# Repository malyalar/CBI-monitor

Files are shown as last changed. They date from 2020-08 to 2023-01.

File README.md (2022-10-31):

# Hematuria monitor

## An open source solution for management and automation of continuous bladder irrigation using off-the-shelf consumer electronics.
Continuous bladder irrigation (CBI), or bladder washout, is a procedure to prevent blood clot formation after urological procedures (prostatic resection, kidney stone removal, et cetera). We believe the process can be augmented through digitized color recognition and wireless updates to the CBI-supervising provider.

## Description
This hematuria monitor ("HM") is an Arduino-controlled device that measures saline flow from the Foley catheter input, through the bladder, and to the outflow collection bag with a load sensor (HX711), and analyzes the absorptivity of outflow irrigate at multiple wavelengths with a visible-light spectrophotometer (AS7262) to non-invasively detect hematuria in the irrigate. It integrates these two datasets to estimate a variety of statistics about the CBI process. In it's current implementation, it can send updates to a custom-built local radio pager (enclosure CAD available, but schematics pending) using a 315mHz transmitter/receiver combo. 

<p float="left">
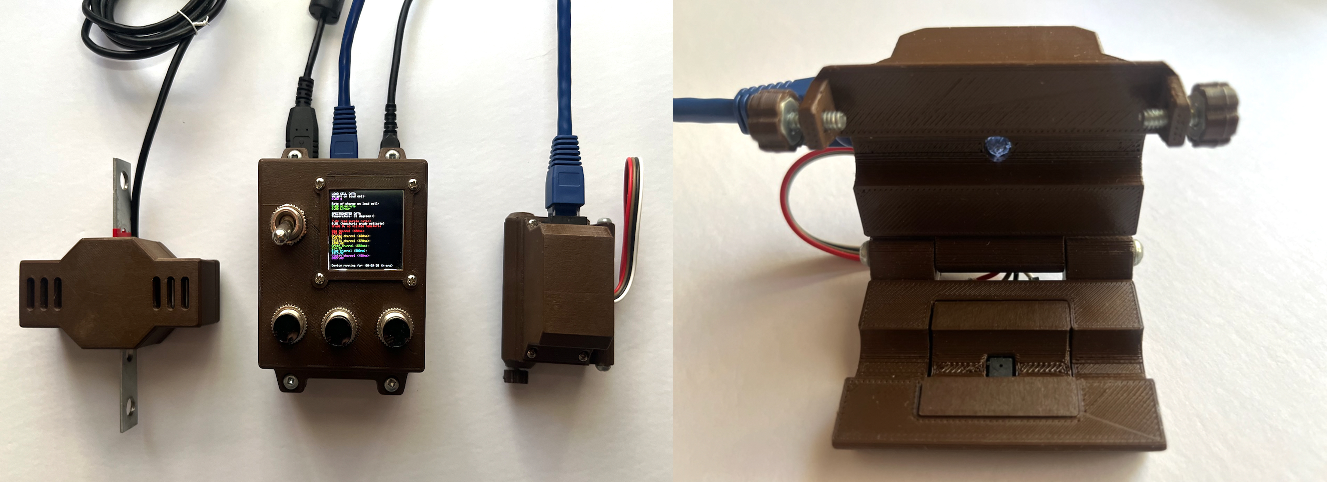
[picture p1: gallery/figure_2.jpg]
  
</p>

Currently, the device can measure and display estimates of:
- estimates hematuria grade;
- total saline used, and rate of collection bag filling;

Future functionality for the device may include motor control to automatically titrate catheter inflow as the estimated rate of blood loss increases, although this is challenging since there may be some clinical considerations other than the observed rate of hematuria that may influence the chosen irrigation rate. Verification and validation processes for controlling the flow rate are also more intense and become harder to justify with respect to medical device regulations.

## Assembly
Assembly guides are pending. 

CAD files are parametric and can be modified to accommodate larger/smaller Arduino/other microprocessor units, buttons, displays, etc. The .stl files used in our device build are provided as well, but work only with the specific buttons, switches, and displays we've purchased. Specific electrical schematics are available but subject to change. Current calibration is based on absorbance through a Baxter Y-type TUR/Bladder Irrigation Set.

## Operation
Every loop (operating at approximately 3s intervals) the load sensor tracks weight and change in weight, and the spectrophotometer tracks absorbance at six spectral channels, spaced at 450, 500, 550, 570, 600 and 650 nm. Hemoglobin is the primary analyte of interest, but the device overall functions mainly as a colorimeter. The chosen spectral sensing unit for this device, the [AS7262 6-channel Visible Spectral ID device](https://cdn.sparkfun.com/assets/f/b/c/c/f/AS7262.pdf) comes with lifetime-calibrated sensing with minimal drift over time or temperature.

The program sketch operates as follows. Taking ten measurements a second at the load sensor and ten measurements a second at the spectrophotometer, the device builds a moving average of five measurements for both, and compares to the moving averages 1 second ago to calculate rates of change. Using a preset lookup table on serial dilutions of blood in Baxter Y-type clear tubing (you will have to recalibrate the lookup table if using differently colored tubing with the spectrophotometer device), the sketch estimates a hematuria grade from the current absorbance at purple wavelengths.

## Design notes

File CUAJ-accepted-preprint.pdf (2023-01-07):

Title: An open source, non-invasive novel assembly for automated real-time monitoring of

continuous bladder irrigation.

Running title: Open-source automated CBI monitoring.

Introduction: Continuous bladder irrigation (CBI) is a common intervention following

endoscopic manipulations of the GU tracts to prevent clot retention in the early postoperative

phase, or for patients with gross hematuria from other causes (benign prostatic hyperplasia,

bladder tumor, etc). During CBI, effluent colour is assessed subjectively by attending staff, and

adjustments are made to input flow rate to lighten the reddish hue to titrate an adequate irrigative

force within the bladder to prevent excessive hemostasis and consequent clot formation.

However, repeated subjective assessments tend to be labour intensive, lack standardization, and

may be unresponsive to changes in effluent color [1]. Tools such as Hemostick® [2] and the

Hematuria Grading Scale [3] offer one solution but still rely on manual assessments to make

adjustments to CBI flow.

In this letter, we present an open-source, inexpensive assembly to construct an automatic CBI

monitor, featuring 3D-printed enclosures and consumer-accessible hardware (https://github.com/

malyalar/CBI-monitor). We secondarily validated the colorimetric function of the device in a

clinical setting in twenty patients on CBI with agreement analysis versus a human raters. Other

groups have developed automated CBI solutions [4-6], but to our knowledge, none are available

on-market, and none have opened their designs for inspection and further development.

Open source medical devices carry several advantages over traditionally developed hardware,

which include but are not limited to: improved pace of innovation; modifiability for more

specific uses; improved repairability; lower cost; and low potential for vendor lock-in [7].

Methods: The hematuria monitor (HM) is built with openness and expandability as core

principles. The device uses the Arduino open-hardware platform, a popular, easy-to-use

development environment that makes it ideal for prototyping devices. HM was also built with

secondary goals of being easy to construct, and to keep potential cost-per-unit low. Instructions

available on our published openhardware.io page include editable CAD files for 3D-printable

enclosures (Figure 1), circuit schematics, code, and data from validation.

The processing unit for HM is an Arduino Nano V3.0. The spectral sensing module is a white

LED mounted opposite an AS7262 spectrophotometer, passing incident light through a catheter

outflow tube latched inside the spectrophotometer shroud (Figure 2), resulting in a reading of

transmitted light at the spectrophotometer inversely proportional to the level of hematuria.

The current implementation of HM uses a lookup table to estimate outflow colour based on

readings from the violet (450nm) wavelength of light, as internal tests demonstrated the greatest

sensitivity/reliability of this wavelength on the selected spectrophotometer to differentiate grades

of hematuria (not shown). Flow rate is detected through rate-of-change calculations from a load

cell from which the catheter outflow bag is mounted. Readout data is displayed via a small

screen.

We conducted initial laboratory validation of the HM with known serial dilutions of known-

hematocrit pig!s blood, sealed within portions of catheter outflow bag tubing (Figure 3). 8

dilutions were measured in quintuplicate, ranging from 0-1mL in 10mL saline. The range of

these dilutions were corresponding to Lee et al.’s Hematuria Grading Scale (HGS) values of 0-10

[3]. A correlation coefficient analysis was undertaken. We also proceeded to validate the colorimetric function of the device in a ward setting, on twenty patients undergoing CBI. 40

pictures were taken of the spectrophotometer shroud clamped on CBI effluent tubes beside a

copy of the HGS, which were rated by three blinded raters on a scale of 0 to 10. These were

simplified to an ordinal score from 0 to 5 to match the device readout. The mode of the three

human-read grades was taken and compared with device readouts via weighted Kappa. Testing

was done under UBC Clinical Ethics Board certificate H20-02012.

Results and Discussion:

The current iteration of the HM can be used completely externally to an existing CBI setup, and

is notably compact. 3D print files are offered in varied formats for edit-ability in different

software. The device can continuously monitor flow rate. The total lowest-estimate cost for the

HM is approximately 45 CAD at the time of writing (Table 1). Future implementations of the

device would include components to control irritant flow rate and other modules that may

increase the build cost. Figure 2 includes pictures of an exemplar build of the HM.

In laboratory testing, the HM achieved a correlation coefficient of 0.97, p<0.001 (Figure 3). In

clinical validation, the hematuria grade readouts from the HM (mean, SD 1.95/5 " 1.51)

achieved a Kappa statistic of 0.822, p<0.001 (Table 2), indicating high agreement with human

raters (mean, SD 1.62/5 " 1.14).

A hematuria monitor such as the one proposed may help increase patient comfort by reducing

clot retention and catheter blockage during CBI, as well as potentially reducing the more

significant complication of a perforated bladder from unrestricted inflow into an outflow blocked

catheter. HM lends itself well to future CBI automation, as we have demonstrated its ability to

distinguish grades of hematuria analogous to human readouts on standard scales, and providing a

means to control the inflow rates to the CBI system based on HM readings may allow for

improved patient safety, comfort, and reduction in complications, as well as reducing

administrative burden by attending staff. The open-source nature of the device lends itself to easy

extensibility, low cost, and feature-richness.

Regulatory approval challenges are a legitimate concern for open-source medical devices.

However, during the COVID-19 pandemic, effort and interest in establishing pathways for open-

source devices to play a larger role in healthcare has flourished. Canadian examples of efforts in

this space include Glia Medical!s research-validated 3D-printable stethoscope [8], and COSMIC

Medical!s Project Bubble Helmet [9].

Future steps include the addition of a wireless communications module to output alarms to a

user!s cellphone, motor control of flow-rate to automate the CBI process fully, and exploration of

regulatory approval processes.

Key messages:

1.There is an opportunity in medical device development that may be addressed by open source

development strategies.

2.Properly assembled consumer electronics-based sensors can be capable of differentiating

grades of hematuria for research purposes in laboratory or clinical settings.

3.We have demonstrated the development of an open-source device to monitor CBI that may

serve as a platform for refinement or development of future adjuncts in the name of increasing

patient safety.

Table 1. Bill of Materials (BOM).

Table 2. Results of Clinical Validation.

| Component | Quantity | PPU
Central unit | Arduino Nano V3.0-based CH340 Chip Atmega328p Board, with USB Cable | 1 | $5.00
| Momentary push buttons (optional) | 3 | $1.00
| 1.8” TFT display module ST7735 | 1 | $9.00
Spectral sensor | AS7262 6-channel visible light spectral sensor breakout | 1 | $20.00
| White LED | 1 | $0.1
Load cell | TAL220 beam-type load cell | 1 | $5.00
| HX711 load cell amplifier | 1 | $1.00
Connectors, misc. | PLA filament for enclosures | 100g | $1
| Resistors, dupont connectors, solder, other consumables | n/a | $1
Total | | | $45.05
| Average ± standard dev. | Kappa | p-value
Human grades (0 to 5) | 1.65 ± 1.95 | 0.822 | <0.001
Machine grades (0 to 5) | 1.11 ± 1.51

Figure legends:

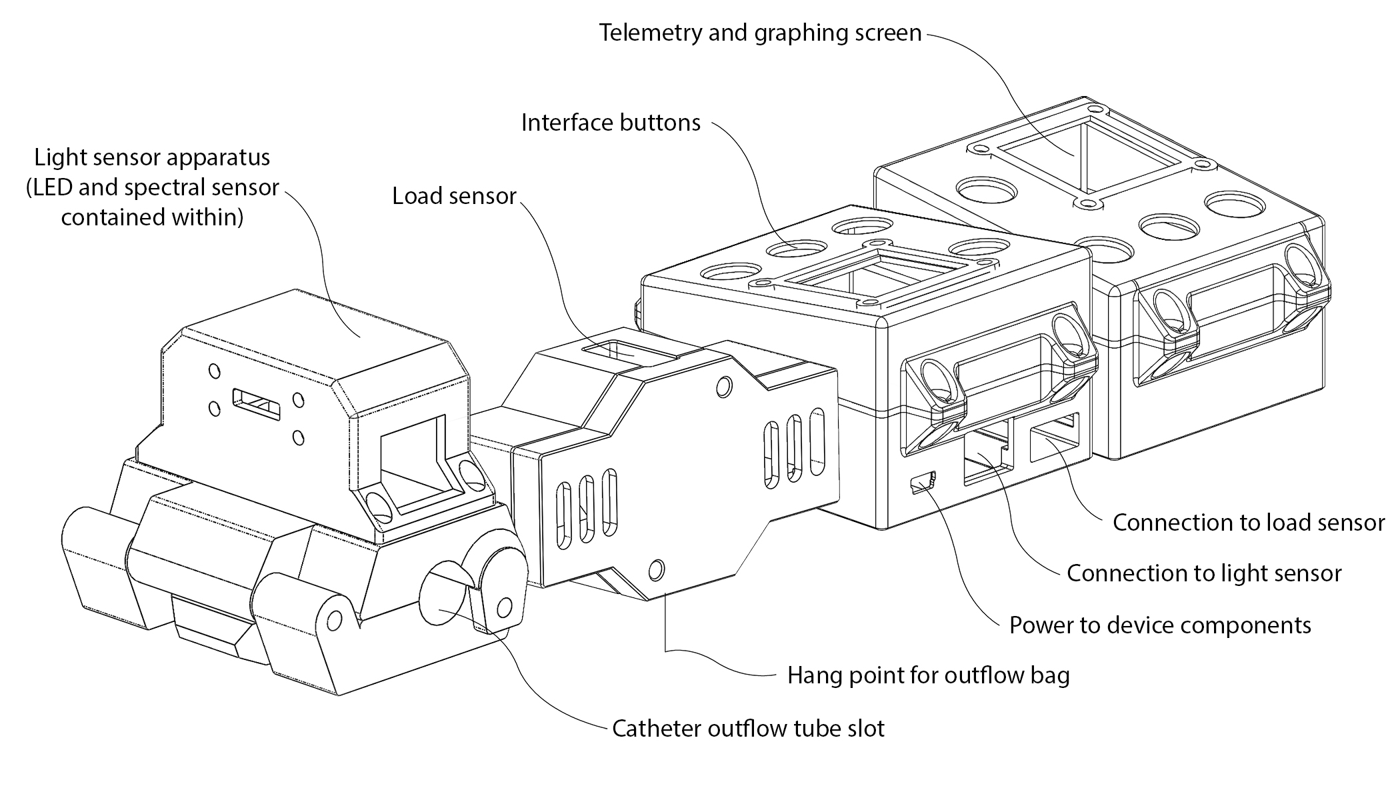
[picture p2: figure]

Figure 1: Wireframe diagrams of 3D printable enclosures of the base model, comprising

three components. 1) A main body with the Arduino Nano microprocessor, with slots for three

buttons, a switch, and a telemetry screen. Next, interfacing with the Arduino through wired

connections: 2) a light sensor apparatus comprising a white LED and the AS7262x spectral

sensing unit mounted opposite to each other within a folding shroud that clips over a catheter

outflow tube, and; 3) a bar-type load sensor (TAL220) with built-in HX711 load cell amplifier

with a hang point for the outflow bag.

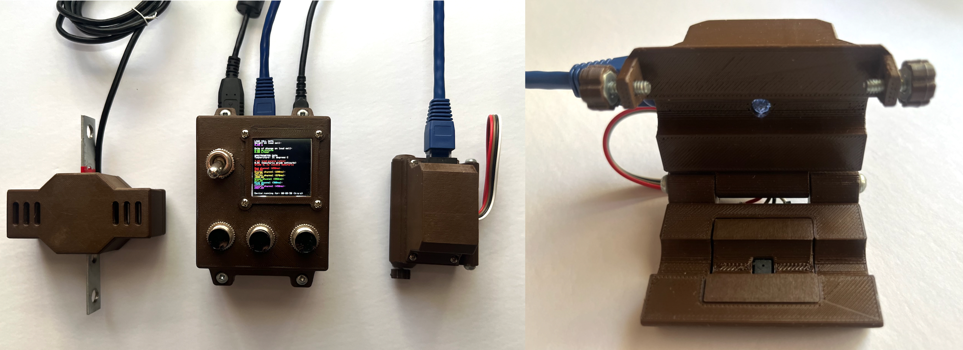
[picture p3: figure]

Figure 2. Demonstration of function of an example build. In view: spectrophotometer shroud

and main processing unit.

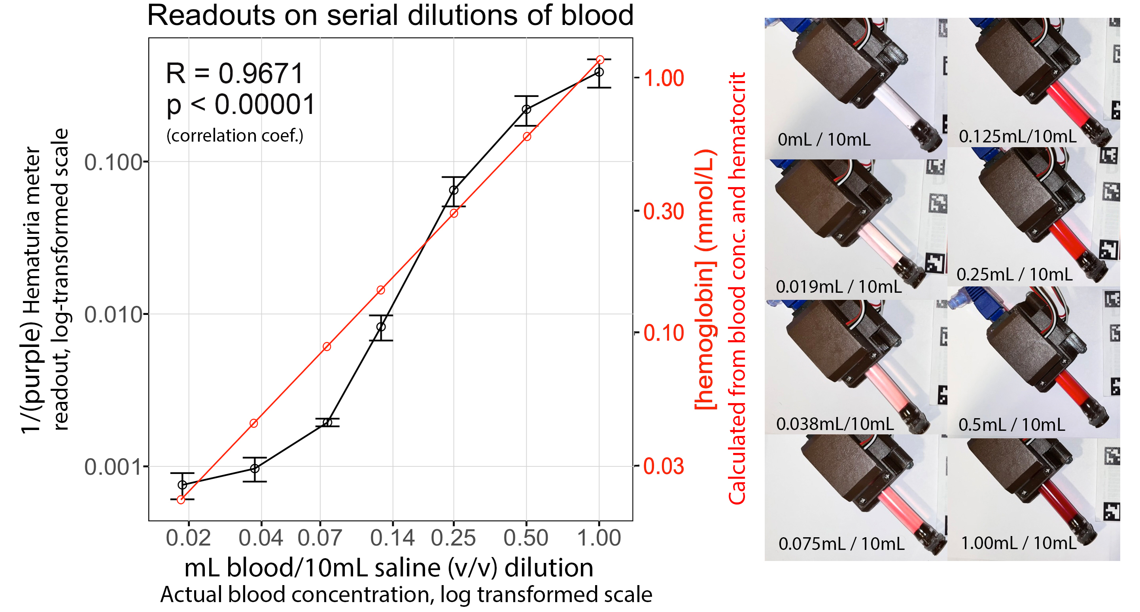
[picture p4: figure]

Figure 3. Validation of hematuria monitor across differing concentrations of blood in CBI

effluent. Eight known volume/volume (mL blood to 10 mL saline) dilutions of thawed,

heparinized pig!s blood in saline were prepared and placed within the spectrophotometer shroud.

On the left y-axis, the internal device calculation based on transmittance at the purple-light

wavelength is shown (arbitrary units). As less purple light reaches the spectral sensor, the device

estimates there is more hemoglobinuria. Internal arbitrary hemoglobinuria estimates from the

device were recorded and plotted alongside values of known dilutions (x-axis is volume/volume

dilution, red y-axis is hemoglobin concentration based on volume and hematocrit), and a

correlation coefficient is shown. An image of the dilution tubes is included for reference to assess

the subjective color range of the tubes.

References:

[1] Drew Phillips, Christopher Nguan. An opportunity for improvement: A novel device to

monitor gross hematuria after urologic surgery. Western Section American Urologic Association

Oct. 2020

[2] Hageman N, Aronsen T, Tiselius HG. A simple device (Hemostick®) for the standardized

description of macroscopic haematuria Our initial experience. Scandinavian journal of urology

and nephrology 2006 Jan 1;40(2):149-54.

[3] Lee JY, Chang JS, Koo KC, Lee SW, Choi YD, Cho KS. Hematuria grading scale: a new tool

for gross hematuria. Urology 2013 Aug 1;82(2):284-9.

[4] Ding A, Cao H, Wang L, Chen J, Wang J, He B. A novel automatic regulatory device for

continuous bladder irrigation based on wireless sensor in patients after transurethral resection of

the prostate: A prospective investigation. Medicine 2016 Dec;95(52).

[5] Yadav N, Rai A, inventors; Baylor College of Medicine, assignee. Autonomous continuous

bladder irrigation devices, colorimeters, and methods of monitoring bladder pressure. United

States patent application US 15/780,389. 2018 Dec 20.

[6] Tan X, Reis G, Stricker D. Convolutional Recurrent Neural Network for Bubble Detection in

a Portable Continuous Bladder Irrigation Monitor. Conference on Artificial Intelligence in

Medicine in Europe 2019 Jun 26 (pp. 57-66). Springer, Cham.

[7] Niezen G, Eslambolchilar P, Thimbleby H. Open-source hardware for medical devices. BMJ

innovations 2016 Apr 1;2(2).

[8] Pavlosky A, Glauche J, Chambers S, Al-Alawi M, Yanev K, Loubani T. Validation of an

effective, low cost, Free/open access 3D-printed stethoscope. PLoS One 2018 Mar

14;13(3):e0193087.

[9] Gusti V, Wu WJ, Grover A, Chiu S, Su KW, Ma E, Chow CK, Sit E, Lim J, Pandhari A, Park
M. The COSMIC Bubble Helmet: A Non-Invasive Positive Pressure Ventilation System for

COVID-19. IEEE Open Journal of Engineering in Medicine and Biology 2020 Nov 9;1:312-5.

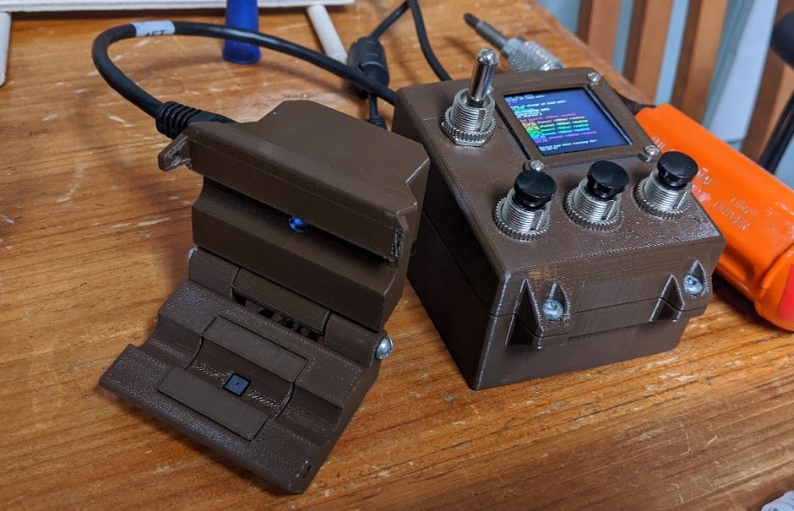
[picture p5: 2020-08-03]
gallery/IMG_20200705_122330_crop.jpg

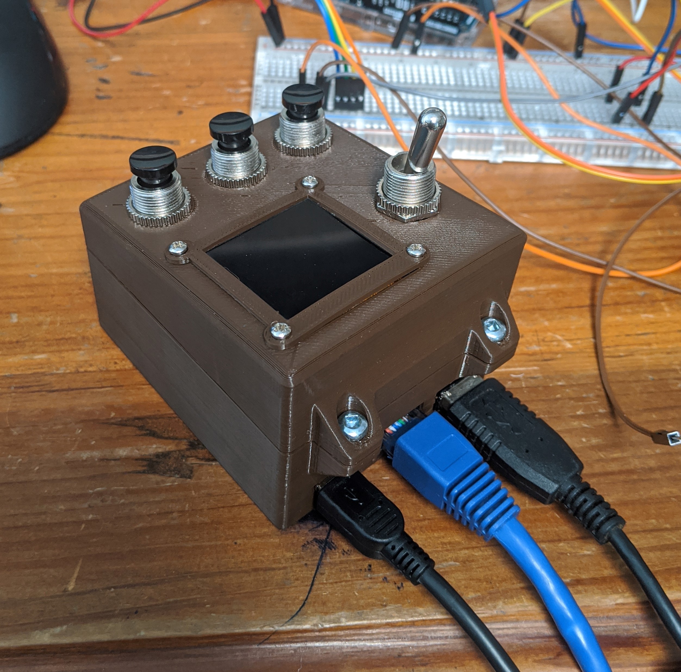
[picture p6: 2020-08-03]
gallery/IMG_20200607_173534_crop.jpg

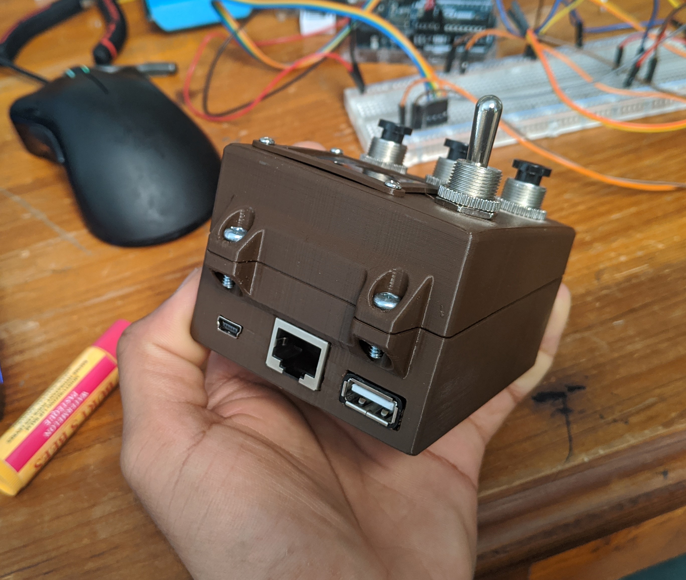
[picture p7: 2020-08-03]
gallery/IMG_20200607_172259_crop.jpg

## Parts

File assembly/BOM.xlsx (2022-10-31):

Bill of Materials, Hematuria Monitor
 | Component | Quantity | PPU | Total
Central Unit | Arduino Nano V3.0-based CH340 Chip Atmega328p Board, with USB Cable | 1 | 3 | 5
 | Momentary push buttons (optional) | 3 | 1 | 3
 | 1.8” TFT display module ST7735 | 1 | 5 | 9
Spectral sensor | AS7262 6-channel visible light spectral sensor breakout | 1 | 20 | 20
 | White LED | 1 | 0.05 | 0.05
Load cell | TAL220 beam-type load cell | 1 | 5 | 5
 | HX711 load cell amplifier | 1 | 0.5 | 1
Connectors, misc | PLA filament for enclosures | 100g | 1 | 1
 | Resistors, dupont connectors, solder, other consumables | N/A | 1 | 1
total |  |  | 33.55 | 45.05

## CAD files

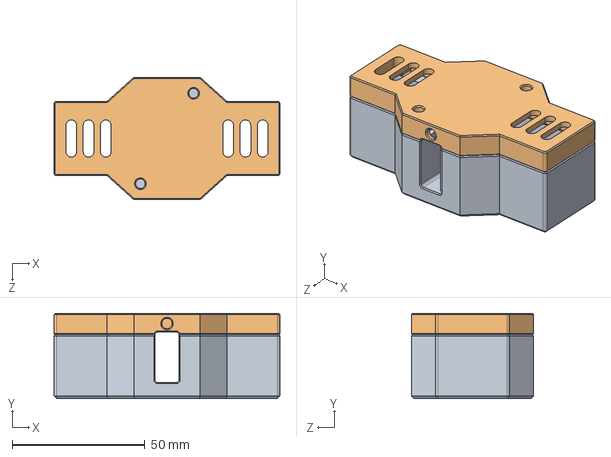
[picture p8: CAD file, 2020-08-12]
assembly/load_sensor/load_sens_assem.SLDASM
85.0 x 32.0 x 46.0 mm
load_sens_body_v3
load_sens_lid

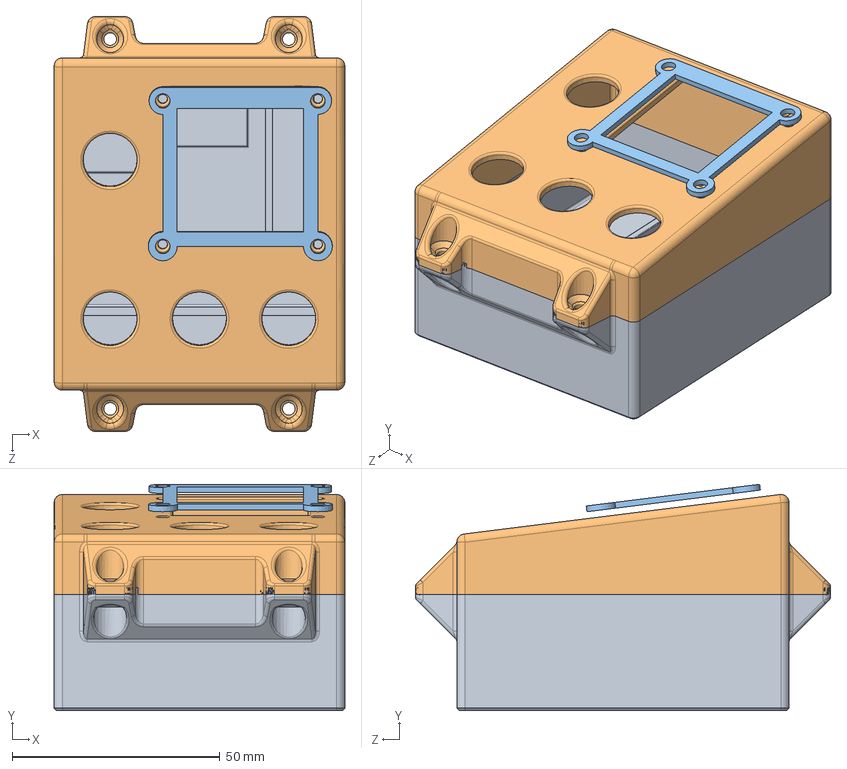
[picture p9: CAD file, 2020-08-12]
assembly/main_unit/Assem2.SLDASM
70.0 x 54.5 x 99.9 mm
enclosure_base_v4
interface_shield_v6
screen_shield

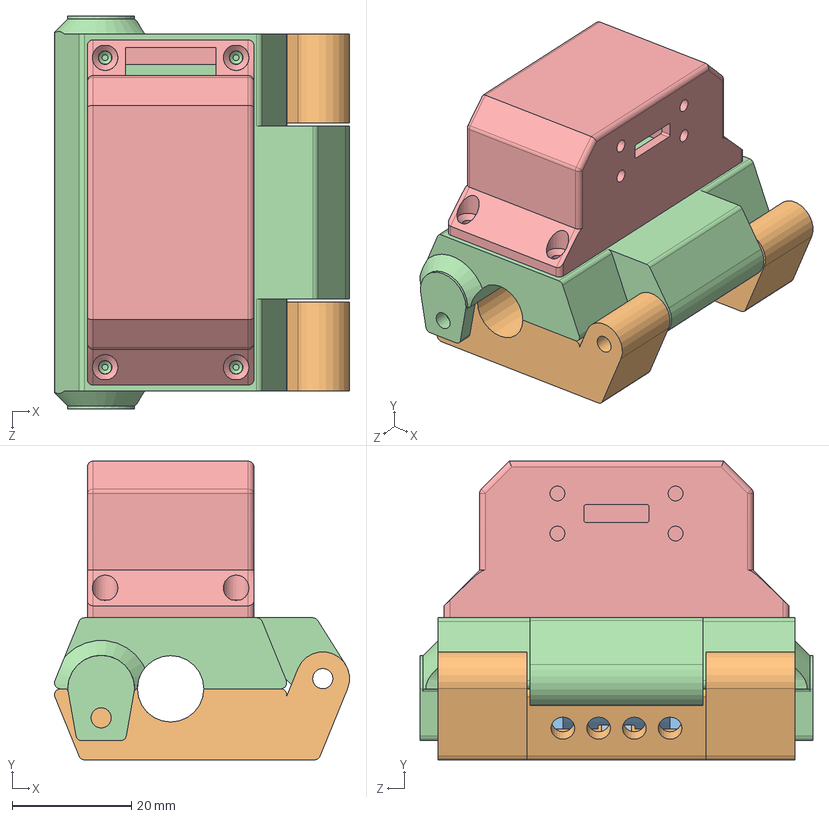
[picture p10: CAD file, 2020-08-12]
assembly/light_sensor/light_sens_assem.SLDASM
49.5 x 50.2 x 66.0 mm
spectral_chip
spectral_shield
spec_top_shield
spec_clip_led+ethernet
spec_clip_ledeth_cap

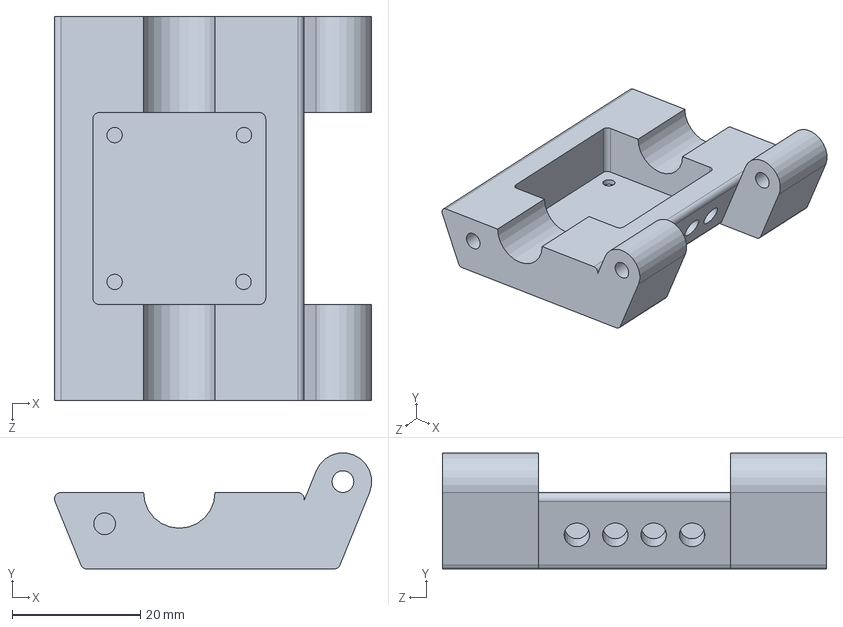
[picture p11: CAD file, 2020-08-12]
assembly/light_sensor/spectral_shield.SLDPRT
49.5 x 18.1 x 60.0 mm

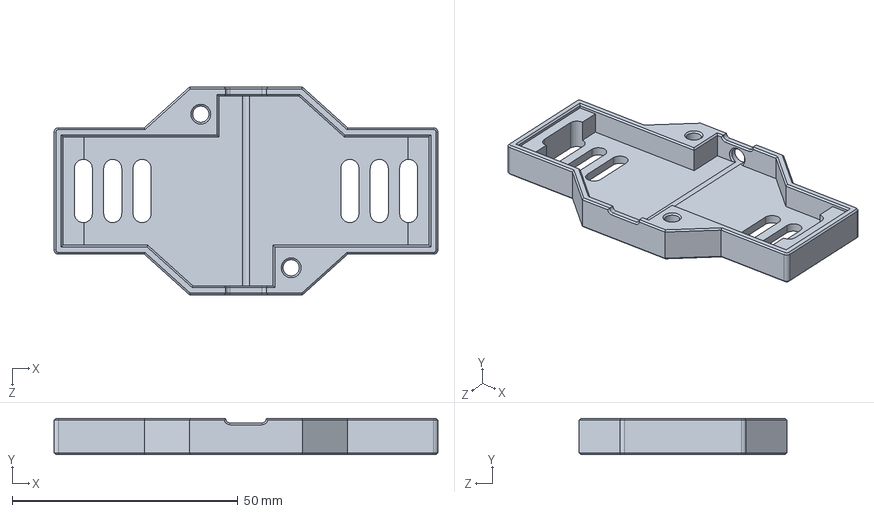
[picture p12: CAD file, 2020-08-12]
assembly/load_sensor/load_sens_lid.SLDPRT
85.0 x 8.00 x 46.0 mm

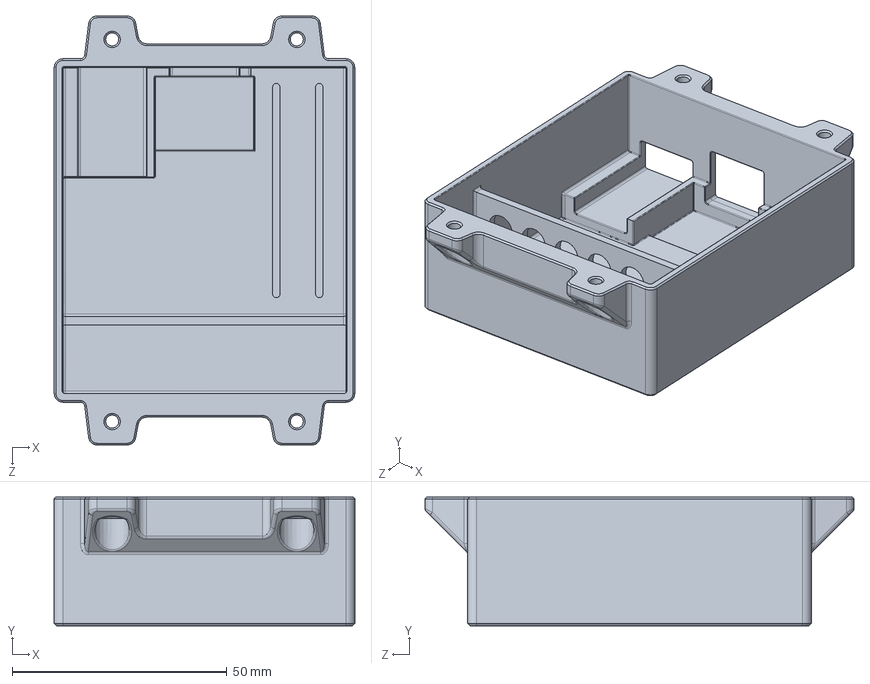
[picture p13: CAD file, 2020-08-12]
assembly/main_unit/enclosure_base_v4.SLDPRT
70.0 x 30.0 x 99.9 mm

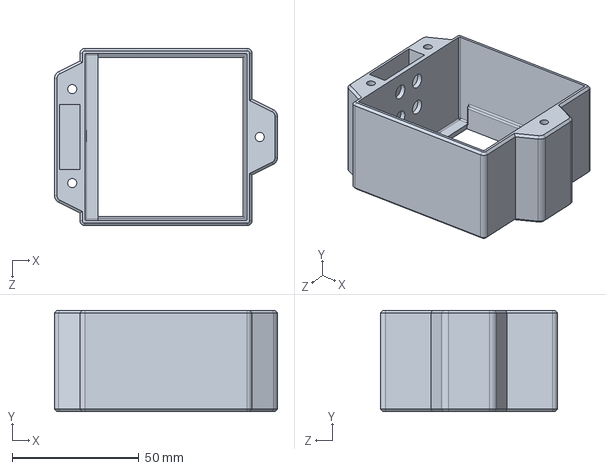
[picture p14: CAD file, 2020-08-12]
assembly/radio_receiver/receiver_base.SLDPRT
88.0 x 40.0 x 70.0 mm

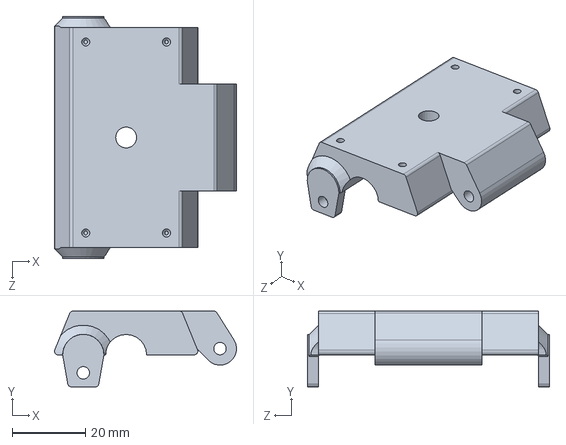
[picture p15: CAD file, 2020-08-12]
assembly/light_sensor/spec_clip_led+ethernet.SLDPRT
49.5 x 20.6 x 66.0 mm

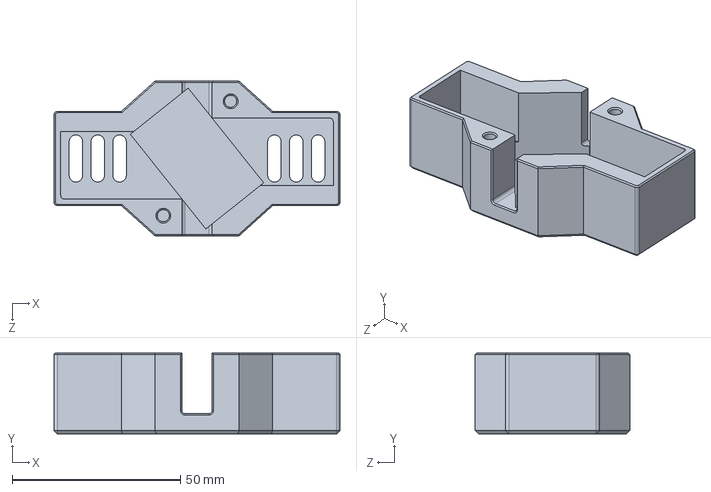
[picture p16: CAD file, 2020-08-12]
assembly/load_sensor/load_sens_body_v3.SLDPRT
85.0 x 24.0 x 46.0 mm

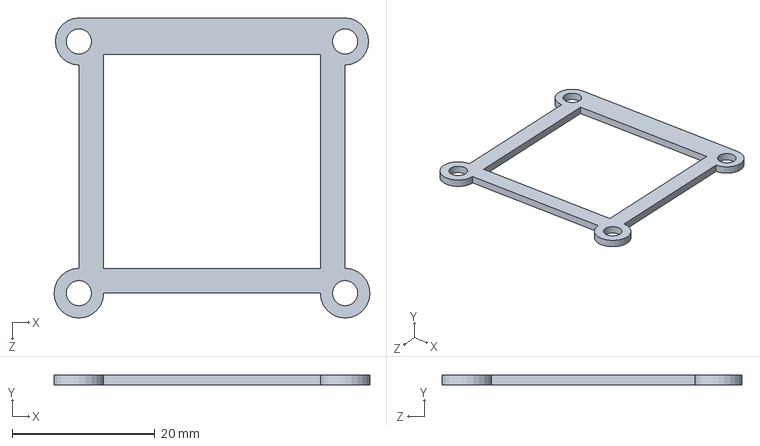
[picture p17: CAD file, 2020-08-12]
assembly/main_unit/screen_shield.SLDPRT
44.3 x 1.40 x 42.1 mm

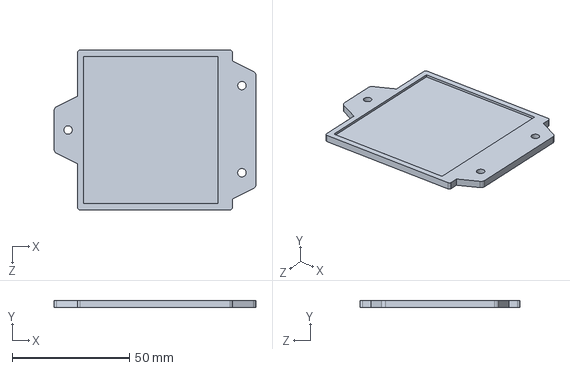
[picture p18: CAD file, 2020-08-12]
assembly/radio_receiver/receiver_batterycover.SLDPRT
86.0 x 3.00 x 68.0 mm

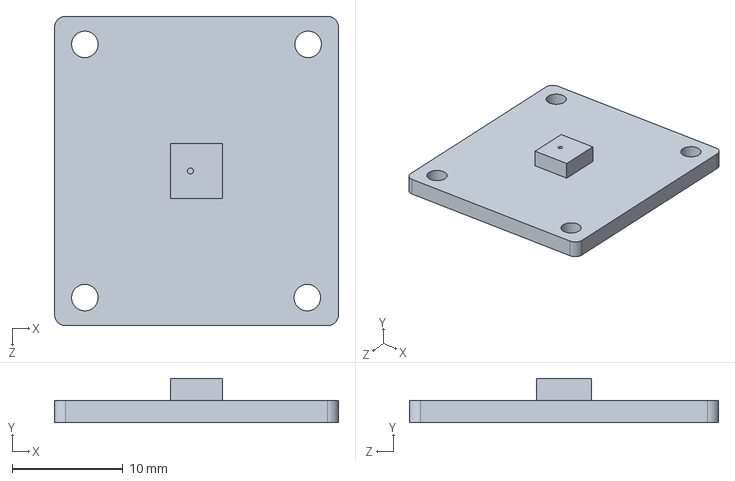
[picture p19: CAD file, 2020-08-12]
assembly/light_sensor/spectral_chip.SLDPRT
25.7 x 4.00 x 28.0 mm

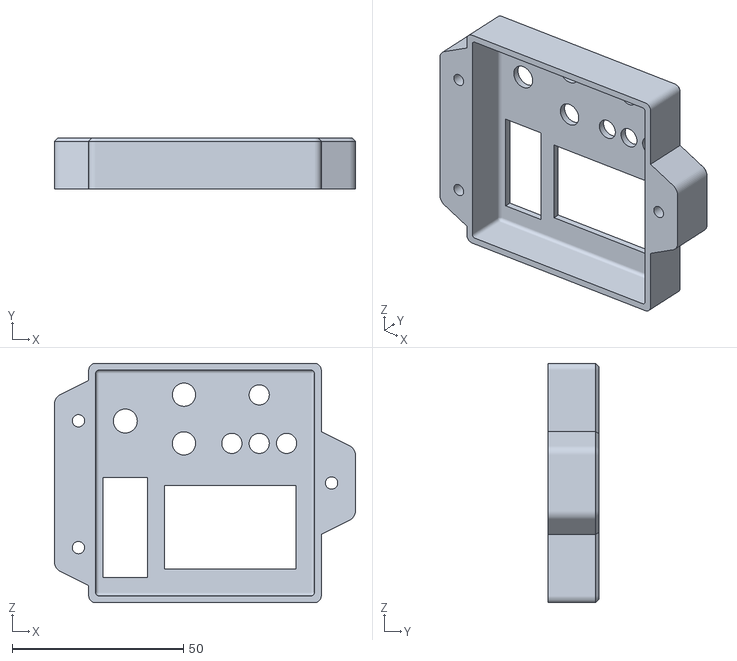
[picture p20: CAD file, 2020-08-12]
assembly/radio_receiver/receiver_sm_faceplate.STL
88.0 x 15.0 x 70.0

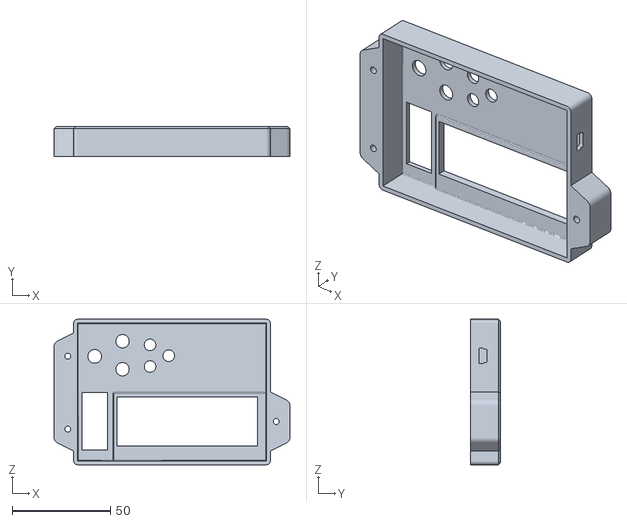
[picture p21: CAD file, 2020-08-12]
assembly/radio_receiver/receiver_faceplate.STL
120.0 x 15.0 x 74.0

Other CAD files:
assembly/radio_receiver/receiver_batt_base.STL
assembly/light_sensor/spec_top_shield.SLDPRT
assembly/light_sensor/spec_clip_ledeth_cap.SLDPRT
assembly/light_sensor/screw_knob.SLDPRT
assembly/light_sensor/screw_knob.STL
assembly/light_sensor/spec_clip_led+ethernet.STL
assembly/light_sensor/spec_clip_ledeth_cap.STL
assembly/light_sensor/spec_top_shield.STL
assembly/light_sensor/spectral_shield.STL
assembly/load_sensor/load_sens_body_v3.STL
assembly/load_sensor/load_sens_lid.STL
assembly/radio_receiver/receiver_batterycover.STL

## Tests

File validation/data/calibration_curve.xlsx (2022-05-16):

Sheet: curve_01
conc | red650 | orange600 | yellow570 | green550 | blue500 | indigo450 | averages | red | orange | yellow | green | blue | indigo | ratios_to_orange | red | orange | yellow | green | blue | indigo | ratios_avg | red | orange | yellow | green | blue | indigo
0.3ml/10mL | 70 | 38 | 27 | 11 | 30.6 | 22 | 0.3ml/10mL | 89.66666667 | 38.66666667 | 46.66666667 | 19 | 58 | 36.33333333 | 0.3ml/10mL | 1.842105263 | 1 | 0.7105263158 | 0.2894736842 | 0.8052631579 | 0.3142857143 | 0.3ml/10mL | 2.211732712 | 1 | 1.176685887 | 0.4786835971 | 1.459677749 | 0.3938438438
 | 108 | 38 | 67 | 27 | 85 | 51 |  |  |  |  |  |  |  |  | 2.842105263 | 1 | 1.763157895 | 0.7105263158 | 2.236842105 | 0.4722222222
 | 90 | 44 | 36 | 15 | 48 | 31 |  |  |  |  |  |  |  |  | 2.045454545 | 1 | 0.8181818182 | 0.3409090909 | 1.090909091 | 0.3444444444
 | 74 | 39 | 37 | 15 | 41 | 27 |  |  |  |  |  |  |  |  | 1.897435897 | 1 | 0.9487179487 | 0.3846153846 | 1.051282051 | 0.3648648649
 | 105 | 39 | 78 | 28 | 104 | 54 |  |  |  |  |  |  |  |  | 2.692307692 | 1 | 2 | 0.7179487179 | 2.666666667 | 0.5142857143
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

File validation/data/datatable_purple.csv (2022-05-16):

dilution_mmol | dilution_vv | rp_value
0 | 0 | 2489 | dilution | avg_ratio | stdev | trial_01 | trial_02 | trial_03 | trial_04 | trial_05
0 | 0 | 2501 | 0 | 2362.8 | 133.987686 | 2489 | 2501 | 2344 | 2184 | 2296
0 | 0 | 2344 | 0.0188 | 1366.2 | 275.7257696 | 1445 | 1762 | 1103 | 1103 | 1418
0 | 0 | 2184 | 0.0375 | 1055.4 | 152.6410823 | 783 | 1127 | 1138 | 1109 | 1120
0 | 0 | 2296 | 0.075 | 516 | 29.3428015 | 513 | 524 | 555 | 515 | 473
0.022044454 | 0.0188 | 1445 | 0.125 | 124.816 | 23.07310729 | 131 | 126 | 157.9 | 114 | 95.18
0.022044454 | 0.0188 | 1762 | 0.25 | 15.8965 | 2.887249773 | 15.68 | 19 | 16.8 | 16.8 | 11.2025
0.022044454 | 0.0188 | 1103 | 0.5 | 4.704 | 0.93705923 | 4.48 | 5.6 | 3.36 | 5.6 | 4.48
0.022044454 | 0.0188 | 1103 | 1 | 2.688 | 0.613449264 | 2.24 | 2.24 | 3.36 | 2.24 | 3.36
0.022044454 | 0.0188 | 1418
0.043971649 | 0.0375 | 783
0.043971649 | 0.0375 | 1127
0.043971649 | 0.0375 | 1138
0.043971649 | 0.0375 | 1109
0.043971649 | 0.0375 | 1120
0.087943299 | 0.075 | 513
0.087943299 | 0.075 | 524
0.087943299 | 0.075 | 555
0.087943299 | 0.075 | 515
0.087943299 | 0.075 | 473
0.146572165 | 0.125 | 131
0.146572165 | 0.125 | 126
0.146572165 | 0.125 | 157.9
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

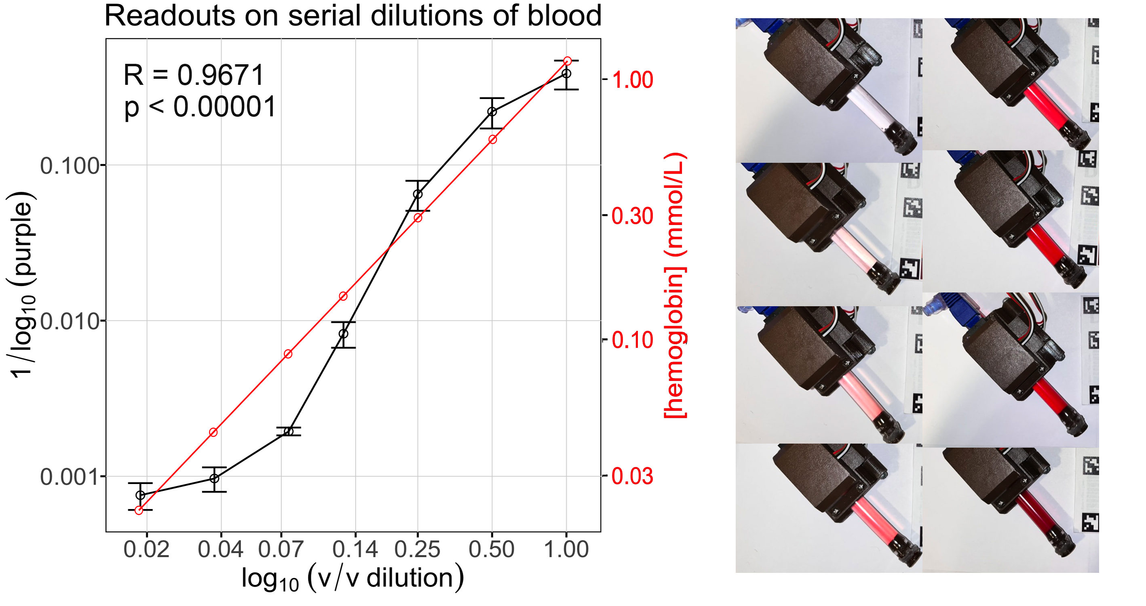
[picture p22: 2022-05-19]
validation/readouts_correlation_invpurple.png

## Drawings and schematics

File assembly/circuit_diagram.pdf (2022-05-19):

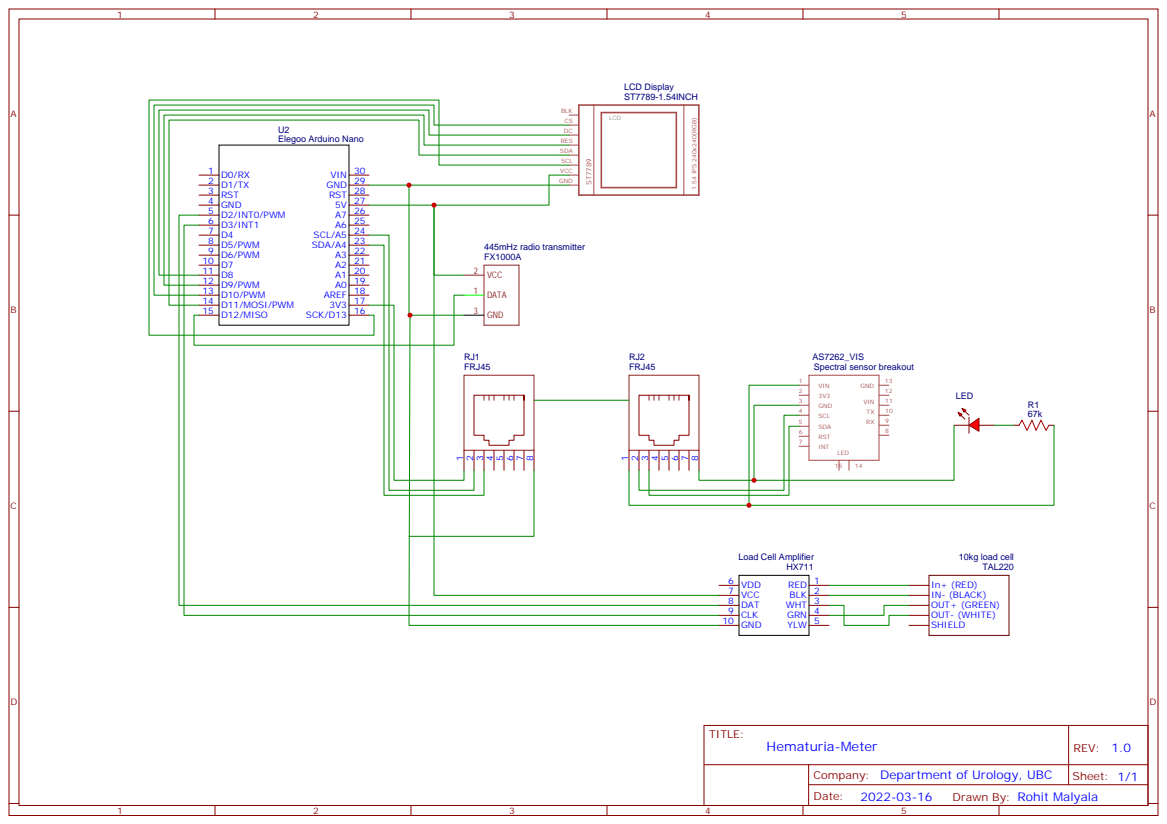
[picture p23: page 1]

Company: Department of Urology, UBC

Drawn By: Rohit Malyala

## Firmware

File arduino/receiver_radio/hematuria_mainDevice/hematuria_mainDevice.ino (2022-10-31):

/******************* 
* Conventional identifying information is anonymized for the purposes of submission.
*******************/

// ---------
// LIBRARIES
// ---------

#include "HX711.h"                    // library for the load calibrated.

#include "Adafruit_AS726x.h"          // library for the spectrophotometer module.
#include <Wire.h>                       // library for I2C communication (aka "Wire").
                                      // library for the TFT display.
#include <Adafruit_GFX.h>               // Core graphics library.
// #include <Adafruit_ST7735.h>            // Hardware-specific library for ST7735
#include <Adafruit_ST7789.h>            // Hardware-specific library for ST7789.
#include <SPI.h>                        // Serial Peripheral Interface (SPI) library.
// #include <SD.h>

// #include "RunningAverage.h"           // running average

                                      // library for the rf module
// Include RadioHead Amplitude Shift Keying Library
#include <RH_ASK.h>

// Create Amplitude Shift Keying Object
RH_ASK rf_driver;



//-------------------------
// PINOUTS AND DECLARATIONS
//-------------------------

// Required pins for the HX711 load calibrated circuit
// -----------------------------------------------
#define LOADCELL_DOUT_PIN 2 // in our build, uses a green wire;
#define LOADCELL_SCK_PIN 3  // in our build, uses a white wire;
float trueWeight;
float displayWeight;
HX711 scale;

// Required pins for the TFT display
// ---------------------------------
#define TFT_CS        10
#define TFT_RST        9 // Or set to -1 and connect to Arduino RESET pin
#define TFT_DC         8
Adafruit_ST7789 tft = Adafruit_ST7789(TFT_CS, TFT_DC, TFT_RST);


// Pins and objects for the photodiode module
// ------------------------------------------
Adafruit_AS726x ams;                            //create the object
// uint16_t sensorValues[AS726x_NUM_CHANNELS];     //buffer to hold raw values. Not used in this project (but possibly worth trying out instead of using calibrated values.
float calibratedValues[AS726x_NUM_CHANNELS];  //buffer to hold calibrated values
// List of functions in the AS726x library: https://adafruit.github.io/Adafruit_AS726x/html/class_adafruit___a_s726x.html#abe1784ea3362da5ed976c5bb1637be79

// Global variables for graphing+sd card writing+radio signalling
//---------------------------------------------------------------

struct dataStruct{
    float send_hgbratio ;
    float send_loadrate;
    float send_load;
    // unsigned long counter;
    }myData;

byte tx_buf[sizeof(myData)] = {0};



// SETUP AND INIT SCREEN
// ---------------------

// storage of "temporal window" of 10 data points:
long time_0;
long time_1;
float scale_1;
float loadSlope;
float loadSlopeHourly;
float purple_ratio;

void setup(void) {

  Serial.begin(38400);   // set baud rate

  // Initialize ASK Object
    rf_driver.init();

  tft.init(240, 240);
  tft.fillScreen(ST77XX_BLACK);
  tft.setTextColor(ST77XX_WHITE);
  tft.setCursor(0, 0);

  tft.setTextColor(ST77XX_WHITE, ST77XX_BLACK);
  tft.println(F("Initializing the Open Hematuria Monitor (OHM). Please ensure that the collection bag is empty. Scale is initializing. \n\n"
              "Development supported by Vancouver Coastal Health, Vancouver General Hospital Department of Urological Sciences.\n\n" 
              "Project undertaken and completed in accordance with curriculum requirements for MEDD 419 'FLEX' of the UBC MD Undergraduate under the supervision of Dr. Chris Nguan."));
  
  scale.begin(LOADCELL_DOUT_PIN, LOADCELL_SCK_PIN);
  scale.set_scale(241.f);     // this value is obtained by calibrating the scale with known weights. Edit it if your load calibrated is off.
  scale.tare();               // reset the scale to 0


  //begin and make sure we can talk to the spectral sensor
  if(!ams.begin()){
    // tft.print(F("The device could not connect to the spectral sensor! Please check your wiring."));
    while(1);
  }

  

  // wait four seconds, then flush screen before going into loop function
  delay(3000);
  tft.fillScreen(ST77XX_BLACK);
  

}


// LOOP FUNCTION
// --------------------
/*  this code is set up such that various functions in the section below are called upon in a certain order to display certain types
    of information at a time. The available screens are: 
    
    screenUpdate_rawtextdata(). 
    This shows immediately current sensor data as raw text. It shows the weight sensed on the load sensor; it shows the rate of
    change in the load sensor data (and builds a "flow rate" out of it), and it shows the spectrophotometer (calibrated)
    readings in each of the six measured wavelengths.
*/

void loop() {

  time_0 = millis();
  
  ams.startMeasurement(); //begin a measurement
  
  bool rdy = false;
  while(!rdy){
    delay(5);
    rdy = ams.dataReady();
  }
 
  ams.readCalibratedValues(calibratedValues); 

  
  purple_ratio = calibratedValues[AS726x_VIOLET]/calibratedValues[AS726x_RED];
   
  screenUpdate_rawtextdata();

  time_1=millis();
  scale_1=scale.get_units(20);
  loadSlope=10*round(((scale_1-trueWeight)/(time_1-time_0)*(1000)*(60))/10);
  loadSlopeHourly=loadSlope/1000*60;

  // logarithmic relationship between the purple:red transmittance ratio and hgb color grade intensity.
  // myData.send_hgbratio=-1.84443*log(purple_ratio)+3.1772;
  // new formula uses exponential regression b/c no axis intercepts theoretically possible
  myData.send_hgbratio=7.90445*pow(0.37612, purple_ratio);
  myData.send_loadrate=loadSlopeHourly;
  myData.send_load=scale_1; 

  memcpy(tx_buf, &myData, sizeof(myData) );
  byte zize=sizeof(myData);
  rf_driver.send((uint8_t *)tx_buf, zize);

  // driver.send((uint8_t *)msg, strlen(msg));
  rf_driver.waitPacketSent();
  
  
}






// "DISPLAYING" FUNCTIONS
// 1: raw text
// 2: graph of load+flow rate
// 3: graph of hematuria grade
// -----------------------------------

void screenUpdate_rawtextdata(){

  // Display load sensor data
  tft.setCursor(0, 0);

  tft.setTextColor(ST77XX_WHITE, ST77XX_BLACK);
  tft.println(F("LOAD CELL DATA"));
  // figure out how to make an underline lol
  tft.println(F("Weight on load cell:"));
  
  trueWeight=scale.get_units(20);
  if (trueWeight<0){
    displayWeight =0;}
  else{
    displayWeight = trueWeight;}
  
  tft.setTextColor(ST77XX_MAGENTA, ST77XX_BLACK);
  tft.print(displayWeight);  
  tft.print(F(" g             "));

  tft.println("");
  tft.setTextColor(ST77XX_WHITE, ST77XX_BLACK);
  tft.println(F("\nRate of change on load cell:"));
  
  tft.setTextColor(ST77XX_GREEN, ST77XX_BLACK);
  tft.print(loadSlope);
  tft.println(F(" mL/minute              "));
  tft.print(loadSlopeHourly);
  tft.print(F(" L/hour                  "));

  //Display spectrophotometer data. While loop included at start is to "wait" until data is available.
    uint8_t temp = ams.readTemperature();
  
  // alternatively: 
  // ams.readRawValues(sensorValues);

  tft.println("\n");
  tft.setTextColor(ST77XX_WHITE, ST77XX_BLACK);
  tft.println(F("SPECTROMETER DATA"));
  tft.print(F("Temperature: "));
  tft.print(temp);
  tft.println(F(" degrees C\n"));
  
  tft.setTextColor(ST77XX_RED, ST77XX_BLACK);
  tft.print(purple_ratio);
  tft.println(" (red:purple ratio)        ");
  float regression_grade_est = 7.90445*pow(0.37612, purple_ratio);
  
  tft.setTextColor(ST77XX_WHITE, ST77XX_BLACK);
  tft.print(regression_grade_est);
  tft.println(" (hematuria grade estimate)");
  
  //"textual" color grading readout.
  tft.setTextColor(ST77XX_RED, ST77XX_BLACK);
  colorGrade_hematuria();
  print_spectrophotometerValues();
  
  tft.setTextColor(ST77XX_WHITE, ST77XX_BLACK);
  tft.print(F("\n\nDevice running for: "));
  calcDisplayElapsedTime();
  tft.print(" (h:m:s)     ");
 
}

/*
void graph(){
  // read the sensor and map it to the screen height
  int drawHeight = map(loadSlope, 0, 1023, 0, tft.height());

  // print out the height to the serial monitor
  Serial.println(drawHeight);

  // draw a line in a nice color
  tft.line(250, 180, 10);
  tft.line(xPos, tft.height() - drawHeight, xPos, tft.height());

  // if the graph has reached the screen edge
  // erase the screen and start again
  if (xPos >= 160) {
    xPos = 0;
    tft.background(250, 16, 200);
  } else {
    // increment the horizontal position:
    xPos++;
  }

  delay(16);
}
*/


// DATA "OBTAIN/PROCESS" FUNCTIONS

void calcDisplayElapsedTime(){

  long hours=(millis()/(1000)/60/60);
  long minutes=(millis()/1000/60)%60;
  long seconds=millis()/(1000)%60;
  
  if(hours<10){
    tft.print('0');}
  tft.print(hours);
  tft.print(":");
  if(minutes<10){
    tft.print('0');}
  tft.print(minutes);
  tft.print(":");
  if(seconds<10){
    tft.print('0');}
  tft.print(seconds);
  
}

void colorGrade_hematuria(){
  
  if(purple_ratio>=6){
    tft.print(F("Grade 0, no visible hematuria"));
  }
  else if(6>purple_ratio && purple_ratio>=3){
    tft.print(F("Grade 1-2, mild hematuria    "));
  }
  else if(3>purple_ratio && purple_ratio>=1){
    tft.print(F("Grade 3-4: medium hematuria  "));
  }
  else if(1>purple_ratio && purple_ratio>=0.5){
    tft.print(F("Grade 4-5: moderate hematuria"));
  }
  else if(0.5>purple_ratio && purple_ratio>=0.35){
    tft.print(F("grade 6-7, marked hematuria  "));
  }
  else if(0.35>purple_ratio && purple_ratio>=0.0){
    tft.print(F("grade 8+, severe hematuria "));
  }
  else{
    tft.print(F("Hematuria not noted. Error.  "));
  }
}

/*
void sendColorGradeRF(){
   // if changing text outputs, make sure all char outputs are exactly 8 characters. Use spaces to pad out if necessary.
   
   
   if(purple_ratio>=6){
    myData.send_hgbratio=0;
  }
  else if(6>purple_ratio && purple_ratio>=3){
    myData.send_hgbratio=1;
  }
  else if(3>purple_ratio && purple_ratio>=2){
    myData.send_hgbratio=3;
  }
  else if(2>purple_ratio && purple_ratio>=1){
    myData.send_hgbratio=5;
  }
  else if(1>purple_ratio && purple_ratio>=0.40){
    myData.send_hgbratio=7;
  }
  else if(0.45>purple_ratio && purple_ratio>=0.0){
    myData.send_hgbratio=9;
  }
  else{
    myData.send_hgbratio="Err";
  }
  
}
*/

void print_spectrophotometerValues(){
  
  tft.setTextColor(ST77XX_RED, ST77XX_BLACK);
    tft.println(F("\n\nRed channel (650nm):"));
    tft.println(calibratedValues[AS726x_RED]);
  tft.setTextColor(ST77XX_ORANGE, ST77XX_BLACK);  
    tft.println(F("Orange channel (600nm):"));
    tft.println(calibratedValues[AS726x_ORANGE]);
  tft.setTextColor(ST77XX_YELLOW, ST77XX_BLACK);
    tft.println(F("Yellow channel (570nm):"));    
    tft.println(calibratedValues[AS726x_YELLOW]);
  tft.setTextColor(ST77XX_GREEN, ST77XX_BLACK);  
    tft.println(F("Green channel (550nm):"));
    tft.println(calibratedValues[AS726x_GREEN]);
  tft.setTextColor(ST77XX_CYAN, ST77XX_BLACK);  
    tft.println(F("Blue channel (500nm):"));;
    tft.println(calibratedValues[AS726x_BLUE]);
  tft.setTextColor(ST77XX_MAGENTA, ST77XX_BLACK);    
    tft.println(F("Violet channel (450nm):"));
    tft.println(calibratedValues[AS726x_VIOLET]);
}
/*
void screenUpdate_weightgraphs()
void screenUpdate_hematuriagraphs()
*/

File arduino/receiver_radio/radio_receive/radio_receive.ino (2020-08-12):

// Include RadioHead Amplitude Shift Keying Library
#include <RH_ASK.h>
// Include dependant SPI Library 
#include <SPI.h> 
 // include the library code:
#include <LiquidCrystal.h>

// initialize the library with the numbers of the interface pins
LiquidCrystal lcd(12, 10, 5, 4, 3, 2);

// Create Amplitude Shift Keying Object
RH_ASK rf_driver;

struct dataStruct{
  float send_hgbratio ;
  float send_loadrate;
  float send_load;
}myData;


unsigned long previousMillis=0;
const long interval=5000;
bool showRateNotLoad = true;

void setup()
{
    // Initialize ASK Object
    rf_driver.init();
    // Setup Serial Monitor
    Serial.begin(38400);

    // set up the LCD's number of columns and rows:
  lcd.begin(8, 2);
  // Print a message to the LCD.
  lcd.print("UMonitor");
  // set the cursor to column 0, line 1
  // (note: line 1 is the second row, since counting begins with 0):
  lcd.setCursor(0, 1);
  lcd.print("Starting");
  pinMode(6, OUTPUT);    // for yellow led
  pinMode(7, OUTPUT);    // for orange led
  pinMode(8, OUTPUT);    // for red led

  digitalWrite(6, LOW);
  digitalWrite(7, LOW);
  digitalWrite(8, LOW);
  
  delay(1500);
}
 
void loop()
{
    
    unsigned long currentMillis=millis();
    if (currentMillis - previousMillis>=interval){
      previousMillis=currentMillis;
    
        if (showRateNotLoad==true){
          showRateNotLoad=false;
        } else {
          showRateNotLoad=true;
        }
    }

    


    uint8_t buf[RH_ASK_MAX_MESSAGE_LEN];
    uint8_t buflen = sizeof(buf);

    if (rf_driver.recv(buf, &buflen)) // Non-blocking
    {
      int i;

      // Message with a good checksum received, dump it.
      
      rf_driver.printBuffer("Got:", buf, buflen);
      memcpy(&myData, buf, sizeof(myData));
      //Serial.println("");
       
      //Serial.print("press_norm: ");
      //Serial.print(myData.press_norm);
      lcd.setCursor(0, 0);

      if(myData.send_hgbratio>=0 && myData.send_hgbratio<=2){
        digitalWrite(6, LOW);
        digitalWrite(7, LOW);
        digitalWrite(8, HIGH);
      }
      else if(myData.send_hgbratio>2 && myData.send_hgbratio<=4){
        digitalWrite(6, LOW);
        digitalWrite(7, HIGH);
        digitalWrite(8, LOW);
      } 
      else {
        digitalWrite(6, HIGH);
        digitalWrite(7, LOW);
        digitalWrite(8, LOW);
      }
      
      if(myData.send_hgbratio>0){
          lcd.print("HgB:");
          lcd.print(myData.send_hgbratio); 
        }
      else{
          lcd.print("Hg:0W/0Y");
        }
       
      
      lcd.setCursor(0, 1);

      if (showRateNotLoad==true){
        if(myData.send_loadrate<0.00){
          lcd.print("0.00");
          lcd.print("L/hr");  
        } else {
          lcd.print(myData.send_loadrate); 
          lcd.print("L/hr");
        }
      } else {
        if(myData.send_load<0.00){
          lcd.print("0.00");
          lcd.print("mL  ");  
        } else {
          lcd.print(myData.send_load); 
          lcd.print("mL  ");
      }
      }
      
      
       
      //Serial.print("  temp: ");
      //Serial.print(myData.temp);
       
      //Serial.print("  counter: ");
      //Serial.println(myData.counter);
    }
    delay(1000);
    
    
}

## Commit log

2020-08-12 initialize
    totally rewritten readme, documentation pdfs, sldwrks CAD files, BOM, and arduino main sketch.
    Readme gallery images relocated to new "gallery" folder.
    [Assem2.SLDASM, BOM.ods, calibration_curve.ods, enclosure_base_v4.SLDPRT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]
2020-08-12 includes sketches for the RF wireless comms
    for the version of the device where a receiver transmitter combo is used to send and display data wirelessly!
2022-05-16 this is a new comit for what I originally intended
    [calibration_curve.xlsx, datatable_purple.csv]
